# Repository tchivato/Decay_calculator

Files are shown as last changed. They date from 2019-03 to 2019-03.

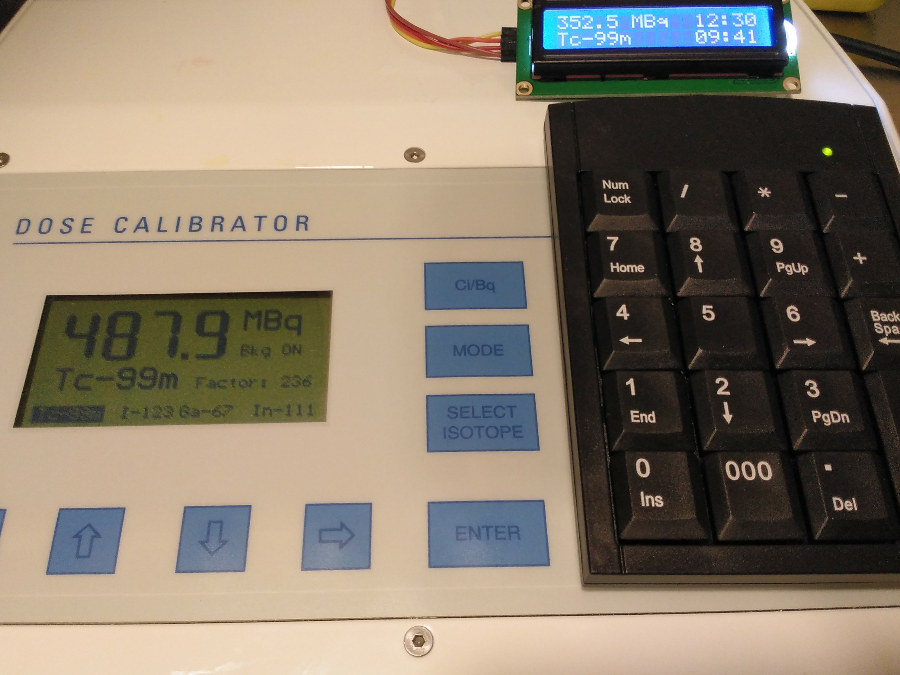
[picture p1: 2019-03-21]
Setup.jpg

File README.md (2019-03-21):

CONTENTS

1. Introduction
2. Setup
3. Operation
4. Troubleshooting
5. References

1 Introduction:

Veenstra's VDC-404 dose calibrator does not have a decay function, operator must use formulas or decay tables to calculate decay.

The Raspberry pi serves as a computer programmed to see in real time the isotope and activity value from the dose calibrator, accept a new time introduced by the operator and show in a display the resulting activity at said time. This eases the operator tasks and reduces errors.

It is programmed for the following isotopes: 99mTc, 123I, 131I, 67Ga, 90Y, 51Cr, 111In and 18F.

2 Setup:

Material list:

-Veenstra VDC-404 dose calibrator.

-Raspberry pi with case. Preferred model is the Zero WH (size and price).

-Micro USB 5V 2.5A power supply.

-Micro SD class 10 card with at least 8 GB loaded with Raspbian.

-Female to female dupont cables:

-Male to female RS232 DB9 null modem cable, without handshake. Male RS232 to male USB, preferably with FTDI chipset.

OR
-Male RS232 to TTL (only option for Raspberry Zero).

-Male to male or female to female RS232 adaptors if the former connectors are not the specified gender.

-USB keypad.

-16x2 LCD with I2C interface.

Boot up the Raspberry pi and enable serial and I2C interface in the configuration menu. 

Install the necessary python 3 modules (1).

Copy the decay.py script into pi directory and modify bashrc to make it run on boot.(2)

Connect the LCD and the RS232 cable or adapter following the schematic provided.

Connect the keypad and the power supply.

Set the RS232 option in the dose calibrator to "PC" and connect it to the Raspberry.

3 Operation:

Boot the Raspberry and wait for the script to load.

Since it has no battery the Raspberry will ask the user to update the time whenever it its switched off. Input time as hhmm.

LCD will show the dose calibrator information: isotope, activity, units and real time in lower right corner.

Operator may introduce a new reference time as hhmm. The program will calculate the resulting activity and display it in the LCD. The new time introduced will show up in the upper right corner of the LCD.

The reference time can be changed again at will. If the keypad is not used in several minutes the display is turned off until a key is pressed.

NOTES:

-The only input accepted by the Raspberry is the time to calculate the decay. Other functions must be done from the dose calibrator itself (changing isotope, units etc).

-Decay is only calculated on the present day, between 00:00 and 24:00. It can calculate forward and backwards in time.

-It is important to check if the real time is accurate so the calculated activity is correct. Pressing <-> allows the user to readjust the real time.

-It is advisable not to turn off the Raspberry unless necessary to prevent data corruption on the SD card. Advanced users may modify log writing on the Raspberry to reduce the card wearing over time.(3)  

4 Troubleshooting:

The 9 pins RS232 cable must be null modem without handshake (just pins 2 and 3 crossed over and pin 5 to ground). Most widespread cables are parallel and will not work since both the dose calibrator and the Raspberry are terminals. It is also not compatible with partial or total handshake, they will cause the dose calibrator to reset.

If there is a malfunction, check that all connections are tight and reset the Raspberry.

If the LCD is blank, adjust its potentiometer to change the contrast.

Most common cause of hardware failure is SD card corruption. Format the card if needed and set it up again or change it for a new card.

As a last option, change the Raspberry.

5 References:

-Veenstra VDC-404 user manual.

-https://github.com/raspberrypi/documentation/blob/master/installation/README.md

-https://github.com/raspberrypi/documentation/blob/master/linux/README.md

(1)Use pip3 to install the following modules if they are not already available: math, os, sys, socket, fcntl, struct, smbus, serial, select, curses. https://help.dreamhost.com/hc/en-us/articles/115000699011-Using-pip3-to-install-Python3-modules

(2)Run on boot (bashrc): http://www.knight-of-pi.org/options-for-autostarting-raspberry-pi-programs-init-d-bashrc-and-cron/

(3)Read only mode: http://hallard.me/raspberry-pi-read-only/

tchivato@hotmail.com

<br /><span xmlns:dct="http://purl.org/dc/terms/" property="dct:title">Dose calibrator decay calculator</span> by <span xmlns:cc="http://creativecommons.org/ns#" property="cc:attributionName">Tomás Chivato</span> is licensed under a <a rel="license" href="http://creativecommons.org/licenses/by-sa/4.0/">Creative Commons Attribution-ShareAlike 4.0 International License</a>.<br />Based on a work at <a xmlns:dct="http://purl.org/dc/terms/" href="https://github.com/tchivato/Decay_calculator" rel="dct:source">https://github.com/tchivato/Decay_calculator</a>.
